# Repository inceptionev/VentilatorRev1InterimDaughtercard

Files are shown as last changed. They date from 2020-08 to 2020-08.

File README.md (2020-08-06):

# Ventilator Rev1 Interim Daughtercard

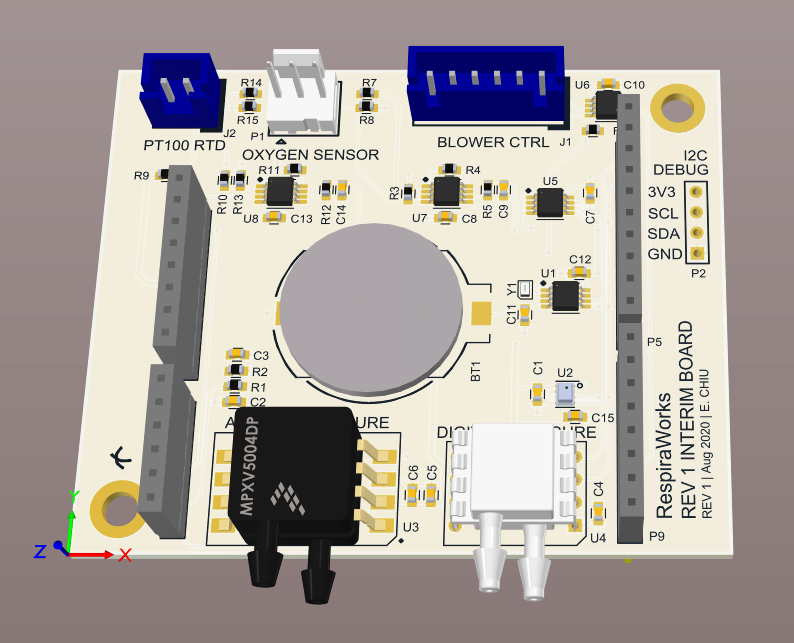
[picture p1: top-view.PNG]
Top View Image


This peripheral board is a development tool designed to provide many of the key features of the Rev A PCB to the current Rev 1.0 PCB

It can stack on top of the stepper drivers in the current Rev 1.0 PCB

Pin definitions, i2c addresses, part datasheets, and scalings are in the [Interface Control Document in GDrive](https://docs.google.com/spreadsheets/d/1JOSQKxkQxXJ6MCMDI9PwUQ6kiuGdujR4D6EJN9u2LWg/edit?usp=sharing)

## The objectives are:
- Allow us to de-risk new circuits and components for the Rev A PCB.
- Allow software devs to code for the new peripherals without waiting for the Rev A PCB.
- Allow us to demo more features in the Current Enclosed Build.
- Take some pressure off the Rev A PCB and give us more time to get it right.

## What's on this board:
- i2c RTC with backup battery
- Higher pressure sensors to allow us to control above 60cmH2O, both a 14b digital and analog option are provided.
- ^ this also frees up the former patient pressure sensor to be used for a 3rd venturi flow meter for oxygen flow sensing.
- 32kbit nonvolatile EEPROM
- Ambient (absolute) pressure sensor for altitude and temperature corrections
- Amplifier for the FiO2 oxygen sensor
- Level-shifted blower control, fixes the blower-full-speed-at-power-up issue: [Issue 740 on Ventilator](https://github.com/RespiraWorks/Ventilator/issues/740).
- Circuit for reading a PT100 RTD temperature sensor, for use such as reading motor or battery temperature.

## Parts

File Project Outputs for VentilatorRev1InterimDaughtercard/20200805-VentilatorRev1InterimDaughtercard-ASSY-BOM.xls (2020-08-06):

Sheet: BOM Report
 |  | Bill of Materials
Source Data From: |  | VentilatorRev1InterimDaughtercard.PrjPcb
Project: |  | VentilatorRev1InterimDaughtercard.PrjPcb
Variant: |  | None
Creation Date: | 8/5/2020 | 3:57 AM
Print Date: | 2020-08-05 | 44048.69839
 | Designator | Description | Value | PCB Package | Manufacturer | Manufacturer P/N | Do Not Populate | Quantity
 | BT1 | CR2016 Coil Cell Battery Holder |  | BLP20 | MPD | BLP2016SM-GTR |  | 1
 | C1, C4, C7, C8, C10, C11, C12, C13, C15 | Cap 0603 | 0.1uF | 603 | Murata | GRM188R71H104KA93D |  | 9
 | C2 | Cap 0603 | 470pF | 603 | Yageo | CC0603MRX7R9BB471 |  | 1
 | C3, C9, C14 | Cap 0603 | 1.5uF | 603 | TDK | C1608X7R1A155K080AC |  | 3
 | C5 | Cap 0603 | 1uF | 603 | Yageo | CC0603KRX7R6BB105 |  | 1
 | C6 | Cap 0603 | 0.01uF | 603 | Samsung | CL10B103KO8NNNC |  | 1
 | J1 | CONN HEADER VERT 6POS 2.5MM |  |  | JST Sales America Inc. | B6B-XH-AM(LF)(SN) |  | 1
 | J2 | CONN HEADER VERT 2POS 2.5MM |  |  | JST Sales America Inc. | B2B-XH-AM(LF)(SN) |  | 1
 | P1 | Conn, KK 0.100" Male Header |  |  | Molex | 22232031 |  | 1
 | P2, P5, P6, P8, P9 | Header, 4-Pin, Tall Female Header 0.100" Pitch 8x1 Sockets, Tall Female Header 0.100" Pitch 6x1 Sockets |  | [NoParam], ESQ-110-14-T-S, ESQ-108-14-T-S, ESQ-106-14-T-S | [NoParam], Samtec |  | DNP | 5
 | R1 | Res 0603 | 1.5k | 603 | Yageo | RC0603FR-071K5L |  | 1
 | R2 | Res 0603 | 3k | 603 | Yageo | RC0603FR-073KL |  | 1
 | R3, R7, R8, R14, R15 | Res 0603 | 10k | 603 | Yageo | RC0603FR-0710KL |  | 5
 | R4, R11 | Res 0603 | 2.05k | 603 | Yageo | RT0603BRD072K05L |  | 2
 | R5, R12 | Res 0603 | 1k | 603 | Yageo | RC0603FR-071KL |  | 2
 | R6 | Res 0603 | 0 | 603 | Yageo | RC0603JR-070RL | DNP | 1
 | R9, R10 | Res 0603 | 3.3k | 603 | Yageo | RT0603BRE073K3L |  | 2
 | R13 | Res 0603 | 80 | 603 | Panasonic | ERA-3AEB80R6V |  | 1
 | U1 | Real Time Clock (RTC) IC Clock/Calendar 64B I²C, 2-Wire Serial 8-TSSOP, 8-MSOP (0.118", 3.00mm Width) |  | 8-MSOP-3.0MM | NXP | PCF85363ATT/AJ |  | 1
 | U2 | Pressure Sensor 4.35PSI ~ 15.95PSI (30kPa ~ 110kPa) Absolute 16b 8-SMD |  | BMP280 | Bosch Sensortec | BMP280 |  | 1
 | U3 | Pressure Sensor 1.45PSI (10kPa) Differential Male - 0.13" (3.3mm) Tube, Dual 0.2 V ~ 4.7 V 8-BSOP (0.475", 12.06mm Width) Dual Ports, Same Side |  | 8-SOP-MPXV | NXP | MPXV5010DP | DNP | 1
 | U4 | Pressure Sensor 1PSI (6.89kPa) Differential Male - 0.14" (3.56mm) Tube, Dual 14 b 8-DIP Module |  | 4525DO | TE Connectivity | 4525DO-DS5AI001DP | DNP | 1
 | U5 | IC EEPROM 256KBIT I2C 400KHZ 8MSOP | 32Kbit | 8-MSOP | Microchip | 24LC256T-I/MS |  | 1
 | U6 | Bidirectional Level Shifter 2-ch |  | 16-TSSOP | Texas Instruments | SN74LVC2T45DCTR |  | 1
 | U7, U8 | Instrumentation Amp, GBW=1MHz |  | 8-VSSOP | Texas Instruments | INA333AIDGKR |  | 2
 | Y1 | CRYSTAL 32.7680KHZ 12.5PF SMD 1x1.6mm | 32.7680KHZ | ABS05-32.768KHZ-T | Abracon | ABS05-32.768KHZ-T |  | 1
 |  |  |  |  |  |  |  | 48

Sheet: Project Information
Project Full Path | C:\Projects\VentilatorRev1InterimDaughtercard\VentilatorRev1InterimDaughtercard.PrjPcb
Project Filename | VentilatorRev1InterimDaughtercard.PrjPcb
Variant Name | None
Data-Source Filename | VentilatorRev1InterimDaughtercard.PrjPcb
Data-Source Full Path | C:\Projects\VentilatorRev1InterimDaughtercard\VentilatorRev1InterimDaughtercard.PrjPcb
Title | Bill of Materials for Project [VentilatorRev1InterimDaughtercard.PrjPcb] (No PCB Document Selected)
Total Quantity | 48
Report Time | 3:57 AM
Report Date | 8/5/2020
Report Date & Tine | 8/5/2020 3:57 AM
Output Name | Bill of Materials
Output Type | BOM_PartType
Output Generator Name | BOM
Output Generator Description | Bill of Materials

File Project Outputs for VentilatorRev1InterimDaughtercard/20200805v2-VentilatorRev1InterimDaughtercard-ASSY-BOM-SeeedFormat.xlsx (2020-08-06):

Designator | Manufacturer Part Number or Seeed SKU | Qty | Link
BT1 | BLP2016SM-GTR | 1 | https://www.digikey.com/product-detail/en/mpd-memory-protection-devices/BLP2016SM-GTR/BLP2016SM-GCT-ND/5430470
C1, C4, C7, C8, C10, C11, C12, C13, C15 | C0603C104M5RACTU | 9 | https://www.digikey.com/product-detail/en/kemet/C0603C104M5RACTU/399-7845-1-ND/3471568
C2 | C0603C471K5RACTU | 1 | https://www.digikey.com/product-detail/en/kemet/C0603C471K5RACTU/399-1075-6-ND/574714
C3, C9, C14 | C1608X7R1A155K080AC | 3 | https://www.digikey.com/product-detail/en/tdk-corporation/C1608X7R1A155K080AC/445-14233-1-ND/3955899
C5 | CC0603KRX7R6BB105 | 1 | https://www.digikey.com/product-detail/en/yageo/CC0603KRX7R6BB105/311-1796-1-ND/5195698
C6 | CL10B103KO8NNNC | 1 | https://www.digikey.com/product-detail/en/samsung-electro-mechanics/CL10B103KO8NNNC/1276-1926-1-ND/3890012
J1 | B6B-XH-AM(LF)(SN) | 1 | https://www.digikey.com/products/en?keywords=B6B-XH-AM(LF)(SN)
J2 | B2B-XH-AM(LF)(SN) | 1 | https://www.digikey.com/product-detail/en/jst-sales-america-inc/B2B-XH-A-M-LF-SN/455-2879-ND/3926507
P1 | 22232031 | 1 | https://www.digikey.com/products/en?keywords=22232031
P2, P5, P6, P8, P9 | DNP | 5
R1 | RC0603FR-071K5L | 1 | https://www.digikey.com/product-detail/en/yageo/RC0603FR-071K5L/311-1-50KHRCT-ND/729811
R2 | RC0603FR-073KL | 1 | https://www.digikey.com/product-detail/en/yageo/RC0603FR-073KL/311-3-00KHRCT-ND/730066
R3, R7, R8, R14, R15 | RC0603FR-0710KL | 5 | https://www.digikey.com/product-detail/en/yageo/RC0603FR-0710KL/311-10-0KHRCT-ND/729827
R4 | RT0603BRD072K05L | 1 | https://www.digikey.com/product-detail/en/yageo/RT0603BRD072K05L/YAG4521CT-ND/6616677
R5, R12 | RC0603FR-071KL | 2 | https://www.digikey.com/product-detail/en/yageo/RC0603FR-071KL/311-1-00KHRCT-ND/729790
R6, R16, R17 | DNP | 1
R9, R10 | RT0603BRE073K3L | 2 | https://www.digikey.com/product-detail/en/yageo/RT0603BRE073K3L/YAG4719CT-ND/6616875
R11 | RT0603BRE073KL | 1 | https://www.digikey.com/product-detail/en/yageo/RT0603BRE073KL/YAG4727DKR-ND/6617879
R13 | ERA-3AEB820V | 1 | https://www.digikey.com/product-detail/en/panasonic-electronic-components/ERA-3AEB820V/P82DBCT-ND/1466026
U1 | PCF85363ATT/AJ | 1 | https://www.digikey.com/product-detail/en/nxp-usa-inc/PCF85363ATT-AJ/568-12408-1-ND/5269686
U2 | BMP280 | 1 | https://www.digikey.com/product-detail/en/bosch-sensortec/BMP280/828-1064-1-ND/6136315
U3 | DNP | 1
U4 | DNP | 1
U5 | 24LC256T-I/MS | 1 | https://www.digikey.com/product-detail/en/microchip-technology/24LC256T-I-MS/24LC256T-I-MSCT-ND/857673
U6 | SN74LVC2T45DCTR | 1 | https://www.digikey.com/product-detail/en/texas-instruments/SN74LVC2T45DCTR/296-16845-1-ND/639461
U7, U8 | INA333AIDGKR | 2 | https://www.digikey.com/product-detail/en/texas-instruments/INA333AIDGKR/296-23564-1-ND/1886116
Y1 | ABS05-32.768KHZ-T | 1 | https://www.digikey.com/product-detail/en/abracon-llc/ABS05-32-768KHZ-T/535-11899-1-ND/3508067

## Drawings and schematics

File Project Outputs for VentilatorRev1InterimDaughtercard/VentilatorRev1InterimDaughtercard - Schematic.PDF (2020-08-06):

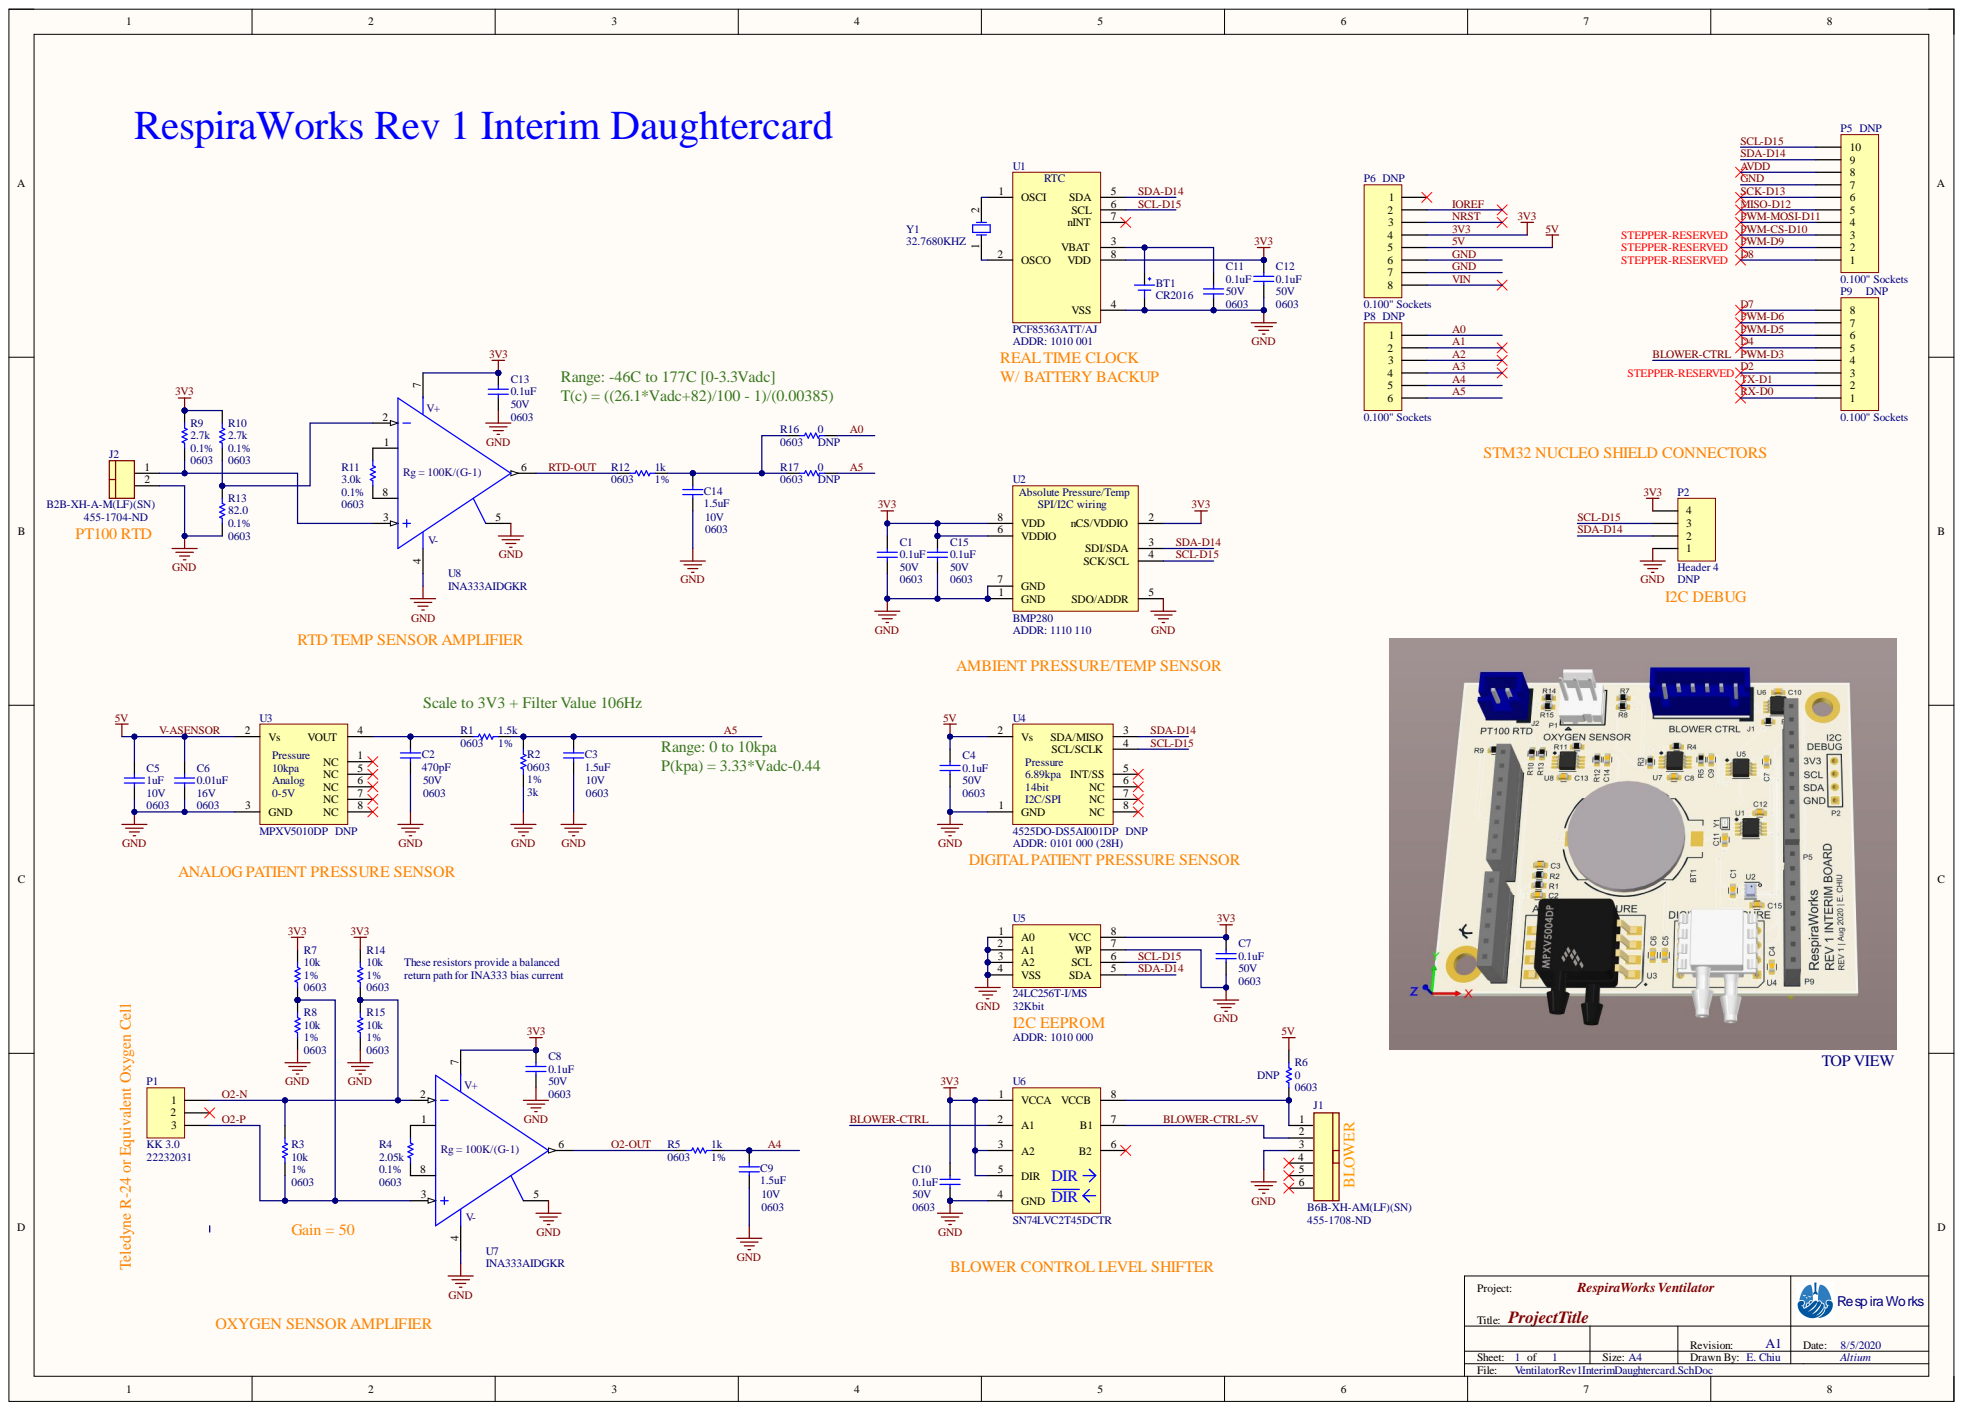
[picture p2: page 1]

RespiraWorks Rev 1 Interim Daughtercard

GND 7

RTD TEMP SENSOR AMPLIFIER

AMBIENT PRESSURE/TEMP SENSOR

Scale to 3V3 + Filter Value 106Hz

GND
DIGITAL PATIENT PRESSURE SENSOR

ANALOG PATIENT PRESSURE SENSOR

These resistors provide a balanced
return path for INA333 bias current

Teledyne R-24 or Equivalent Oxygen Cell

BLOWER CONTROL LEVEL SHIFTER

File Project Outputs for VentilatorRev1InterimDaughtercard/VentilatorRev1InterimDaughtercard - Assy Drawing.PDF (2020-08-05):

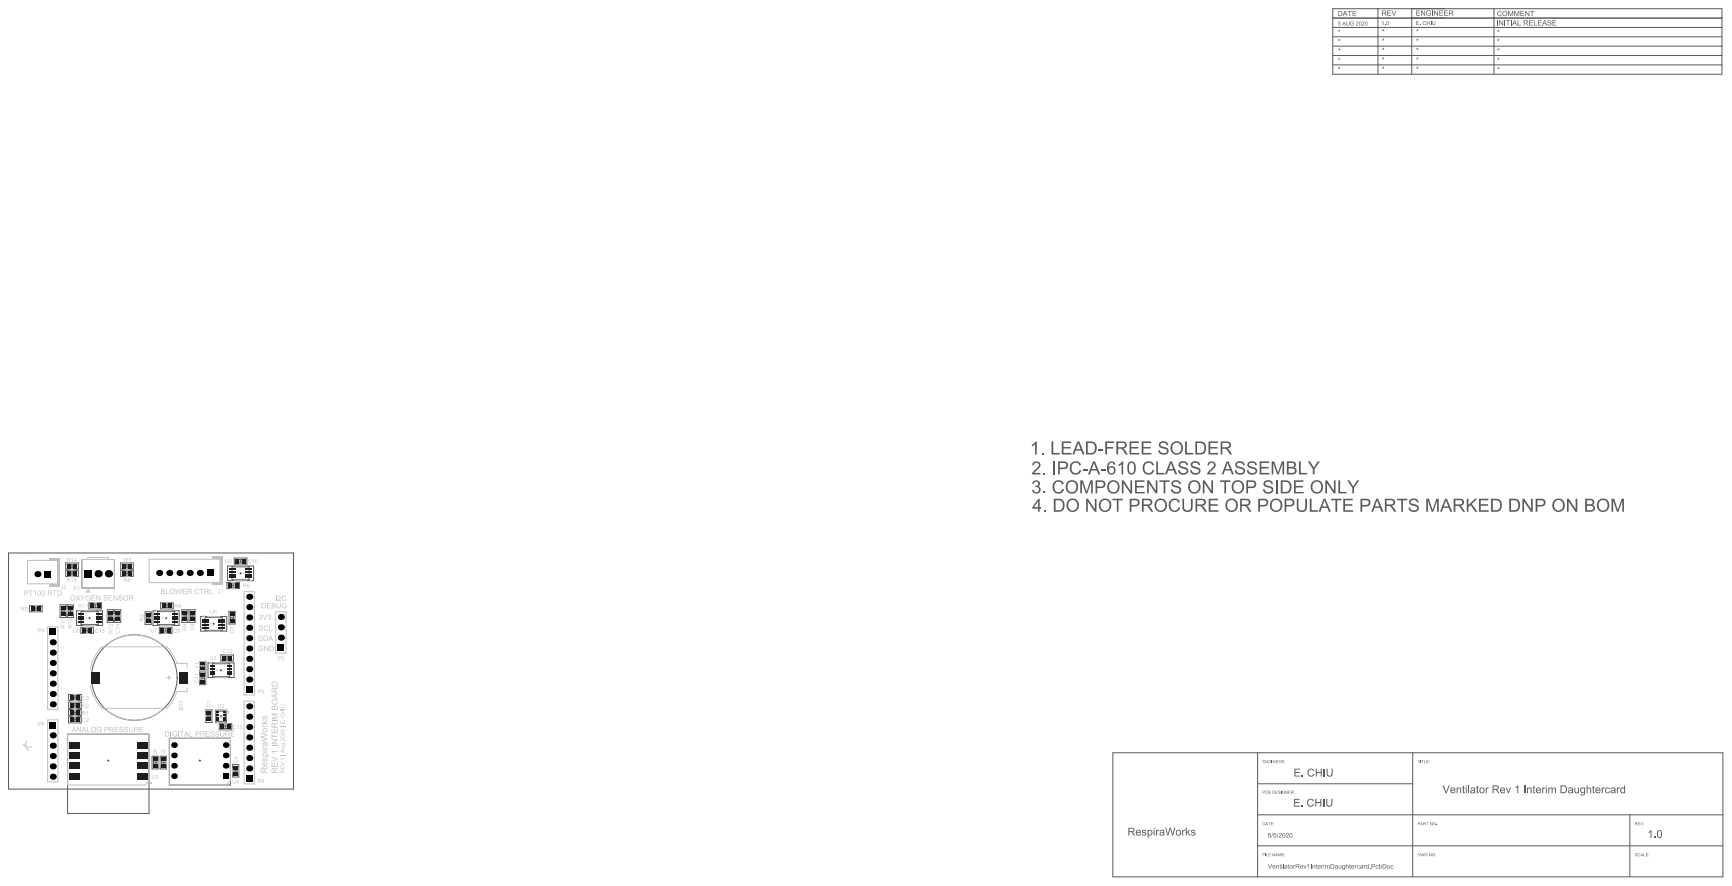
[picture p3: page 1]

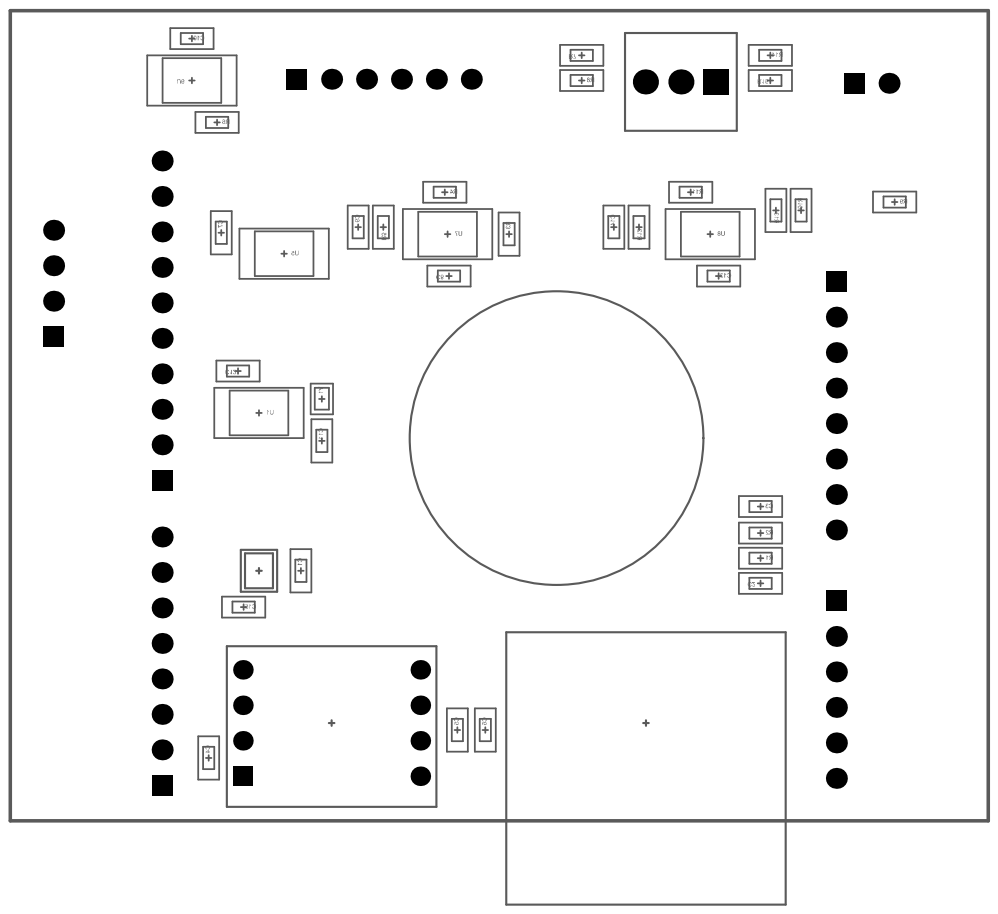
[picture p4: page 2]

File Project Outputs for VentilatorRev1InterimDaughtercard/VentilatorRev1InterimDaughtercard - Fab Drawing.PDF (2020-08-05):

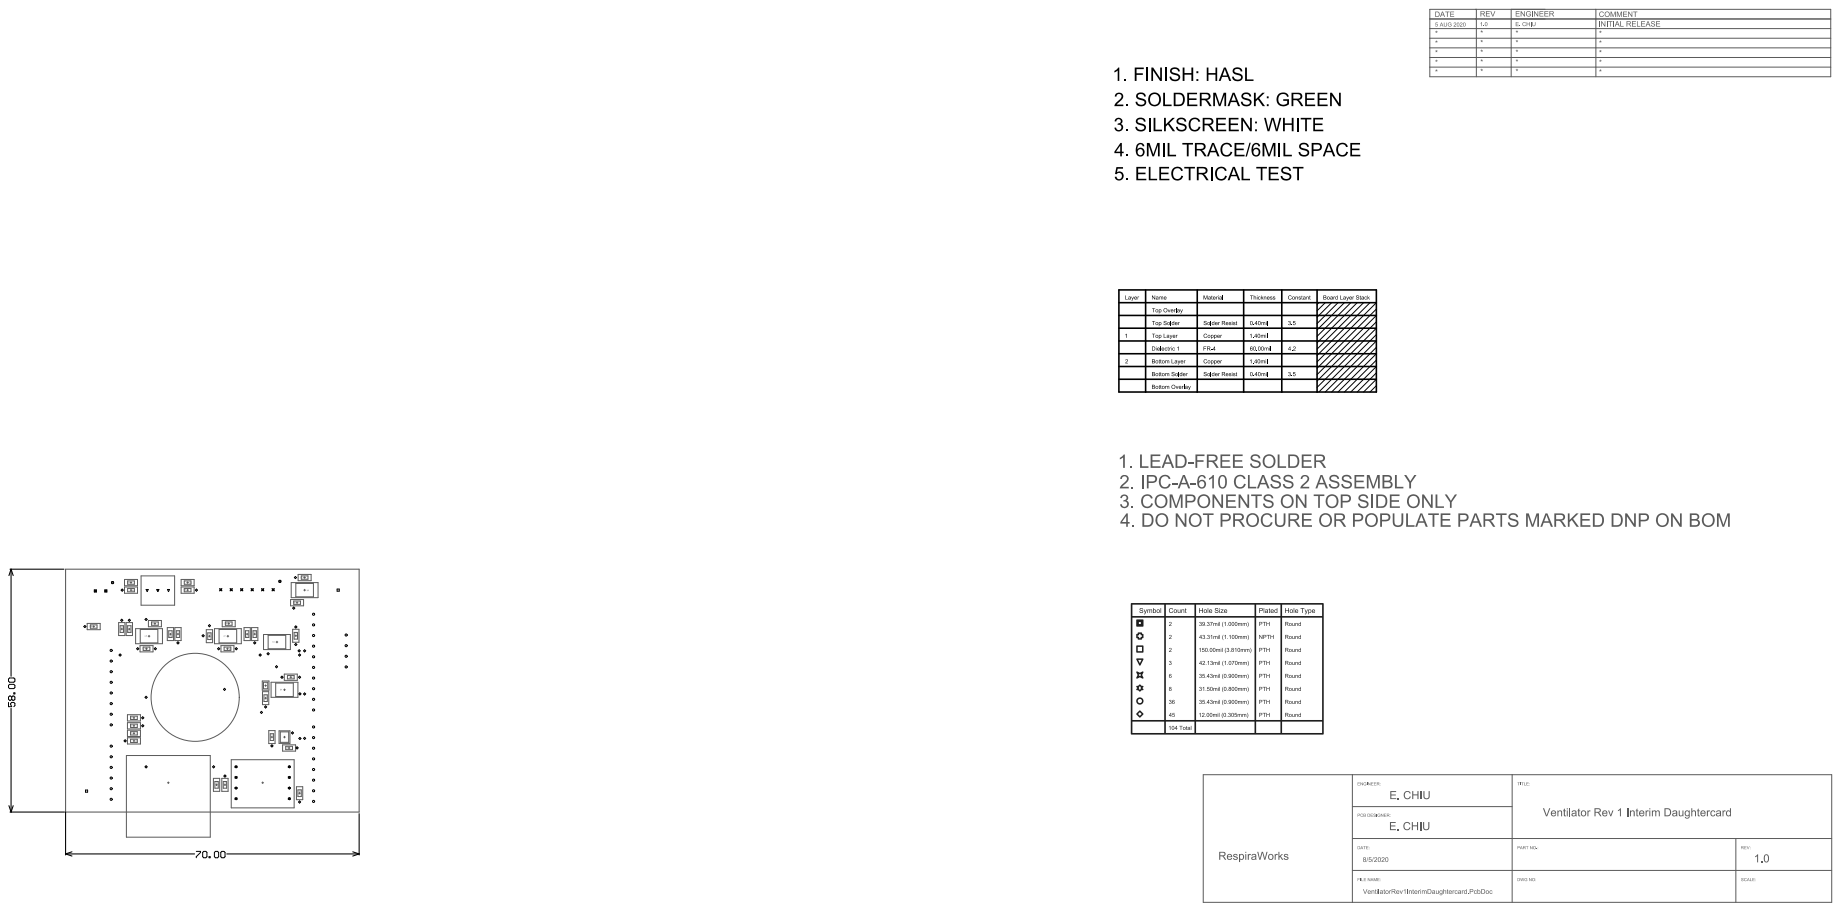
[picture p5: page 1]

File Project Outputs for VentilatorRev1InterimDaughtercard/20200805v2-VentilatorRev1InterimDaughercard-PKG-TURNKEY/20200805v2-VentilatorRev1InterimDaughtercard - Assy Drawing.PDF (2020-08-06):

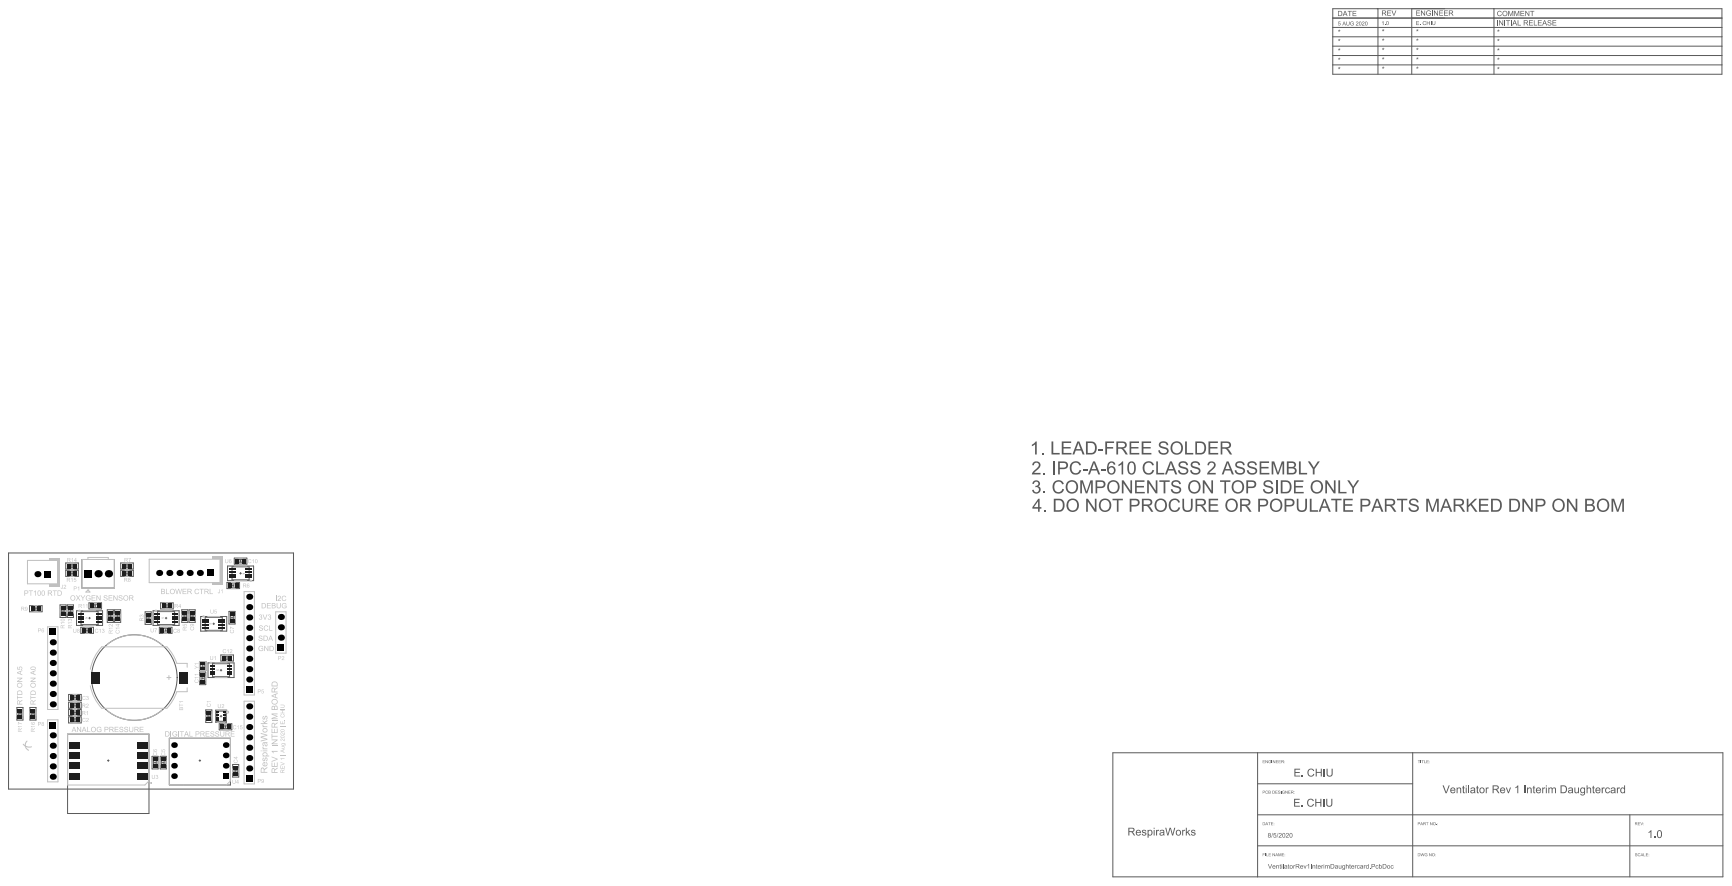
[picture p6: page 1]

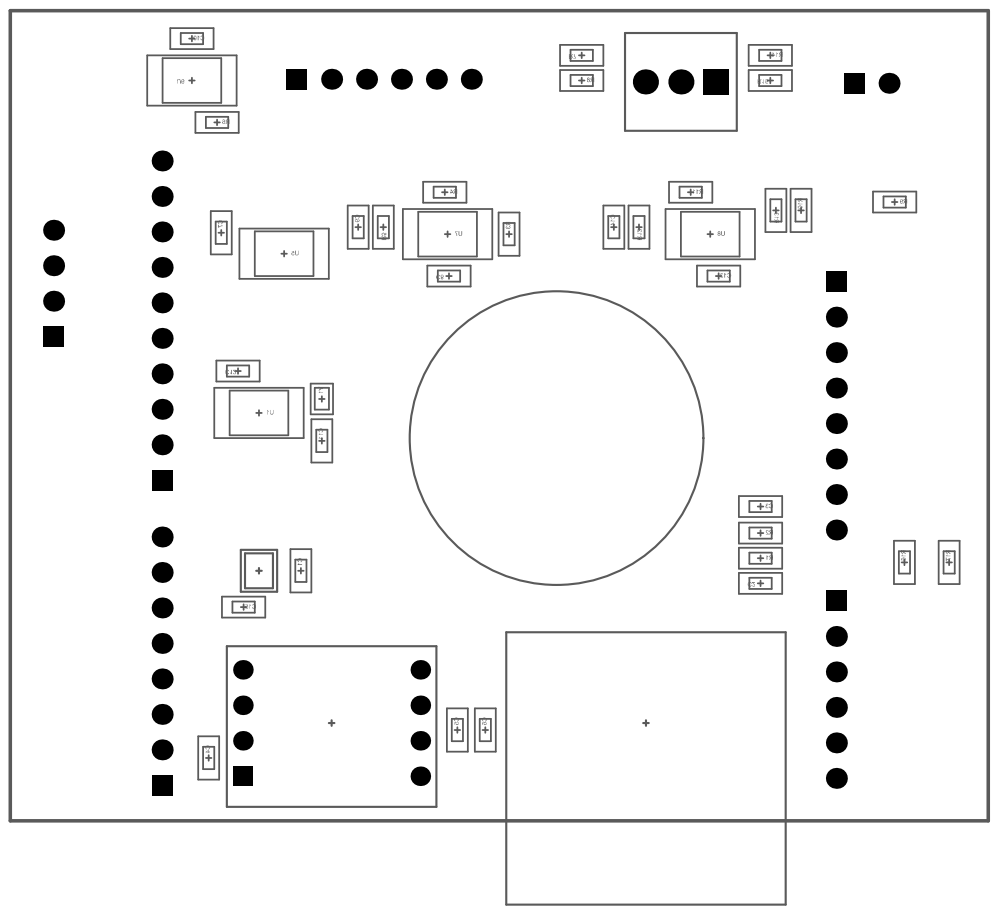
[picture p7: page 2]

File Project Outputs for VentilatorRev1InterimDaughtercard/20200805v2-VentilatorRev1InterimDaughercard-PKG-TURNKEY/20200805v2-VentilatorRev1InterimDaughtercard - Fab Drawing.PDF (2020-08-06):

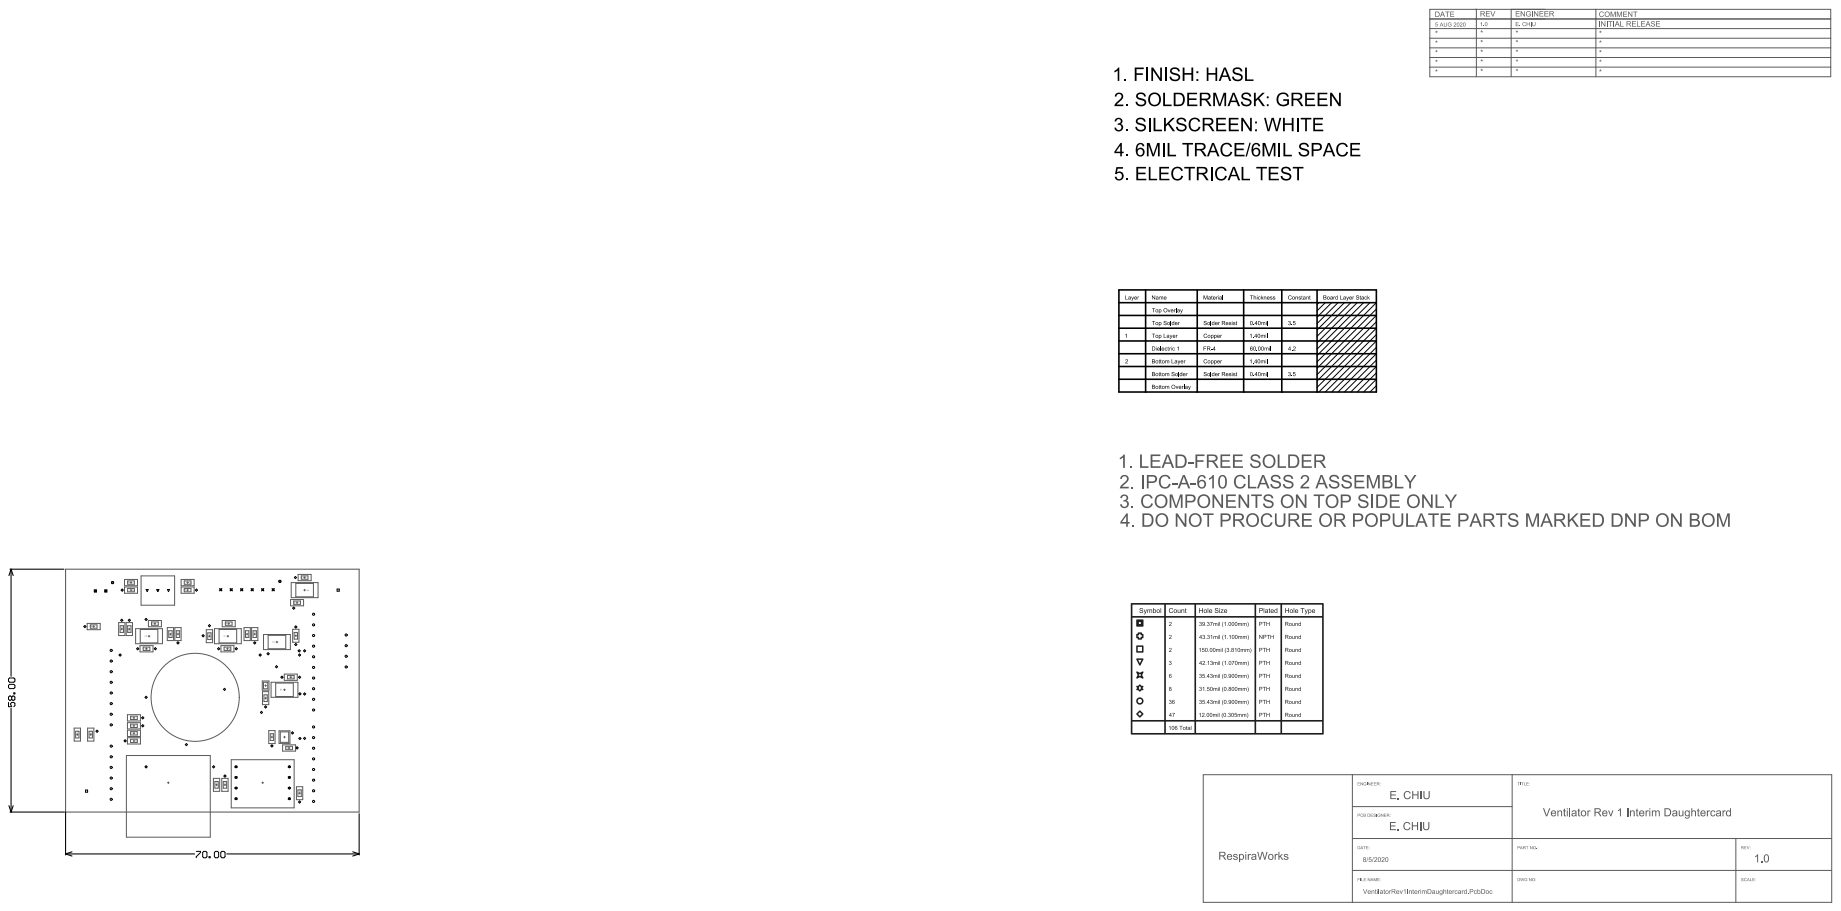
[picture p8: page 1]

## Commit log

2020-08-02 initial creation
    [VentilatorRev1InterimDaughtercard.PcbDoc, VentilatorRev1InterimDaughtercard.PrjPcb, VentilatorRev1InterimDaughtercard.SchDoc]
2020-08-03 schematic first pass
    [VentilatorRev1InterimDaughtercard.PcbDoc, VentilatorRev1InterimDaughtercard.SchDoc]
2020-08-03 compile and annotation
    [VentilatorRev1InterimDaughtercard.PrjPcb, VentilatorRev1InterimDaughtercard.SchDoc]
2020-08-05 added and placed RTD circuit
    [VentilatorRev1InterimDaughtercard.PcbDoc, VentilatorRev1InterimDaughtercard.SchDoc]
2020-08-05 first pass layout DRC zero
    [VentilatorRev1InterimDaughtercard.PcbDoc, VentilatorRev1InterimDaughtercard.PrjPcb, VentilatorRev1InterimDaughtercard.SchDoc]
2020-08-05 final footprint checks, fixed board guides on XH connectors. Commit before generate mfg files
    [VentilatorRev1InterimDaughtercard.PcbDoc, VentilatorRev1InterimDaughtercard.SchDoc]
2020-08-05 generate manufacturing files
    [20200805-VentilatorRev1InterimDaughtercard-ASSY-BOM-SeeedFormat.xlsx, 20200805-VentilatorRev1InterimDaughtercard-ASSY-BOM.xls, VentilatorRev1InterimDaughtercar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]
2020-08-06 created 20200805v2 to correct 5V digital pressure sensor and analog input contention
    [20200805-VentilatorRev1InterimDaughtercard-ASSY-BOM.xls, 20200805v2-Pick Place for VentilatorRev1InterimDaughtercard.csv, 20200805v2-VentilatorRev1InterimDaugh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]
